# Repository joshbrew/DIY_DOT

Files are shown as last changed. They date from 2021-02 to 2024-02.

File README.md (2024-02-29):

# DIY Diffuse Optical Tomography (DOT) PCB plans

Testing low cost 28 sensor DOT. This repo will be getting updated as I get results and some working code to share. I will share how to drive the LEDs and how I get simultaneous sensor output as I get things demonstrable.

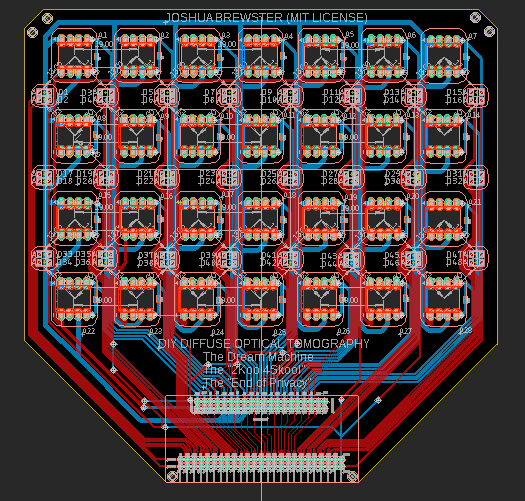
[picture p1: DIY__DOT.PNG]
DIYDOT


DIY DOT flexible sensor design based on [this 2007 Retinotopic mapping paper](https://www.pnas.org/content/104/29/12169) for a simple and modular 28 channel high-density optical tomography headset. The question I want to answer: can I get [deep image reconstruction](https://journals.plos.org/ploscompbiol/article?id=10.1371/journal.pcbi.1006633)?

This design uses 28 OPT101s and 24 pairs (48 total) 1206 sized generic LED pairs of whatever wavelength you want. The OPT101s can have the gain turned up by adding a cap and resistor between the right pins [see datasheet](https://www.ti.com/lit/ds/symlink/opt101.pdf?HQS=TI-null-null-alldatasheets-df-pf-SEP-wwe). You can get really cheap ones on Aliexpress that work consistently.

Use a site like PCBway for cheap flex PCBs. There is FR4 stiffener on both sides. This is meant to be hand-assembled, careful not to burn the pads or sensitive OPT101 pins (i.e. use low temperature solder for testing). Pop the OPT101s (notch facing left from the front) in through the back to make them flush with the stiffener and solder from back.  

# 16 channel (forehead-friendly)

New (cheapo version):
Capture1

New (includes transimpedance amps):
Capture2

Old:
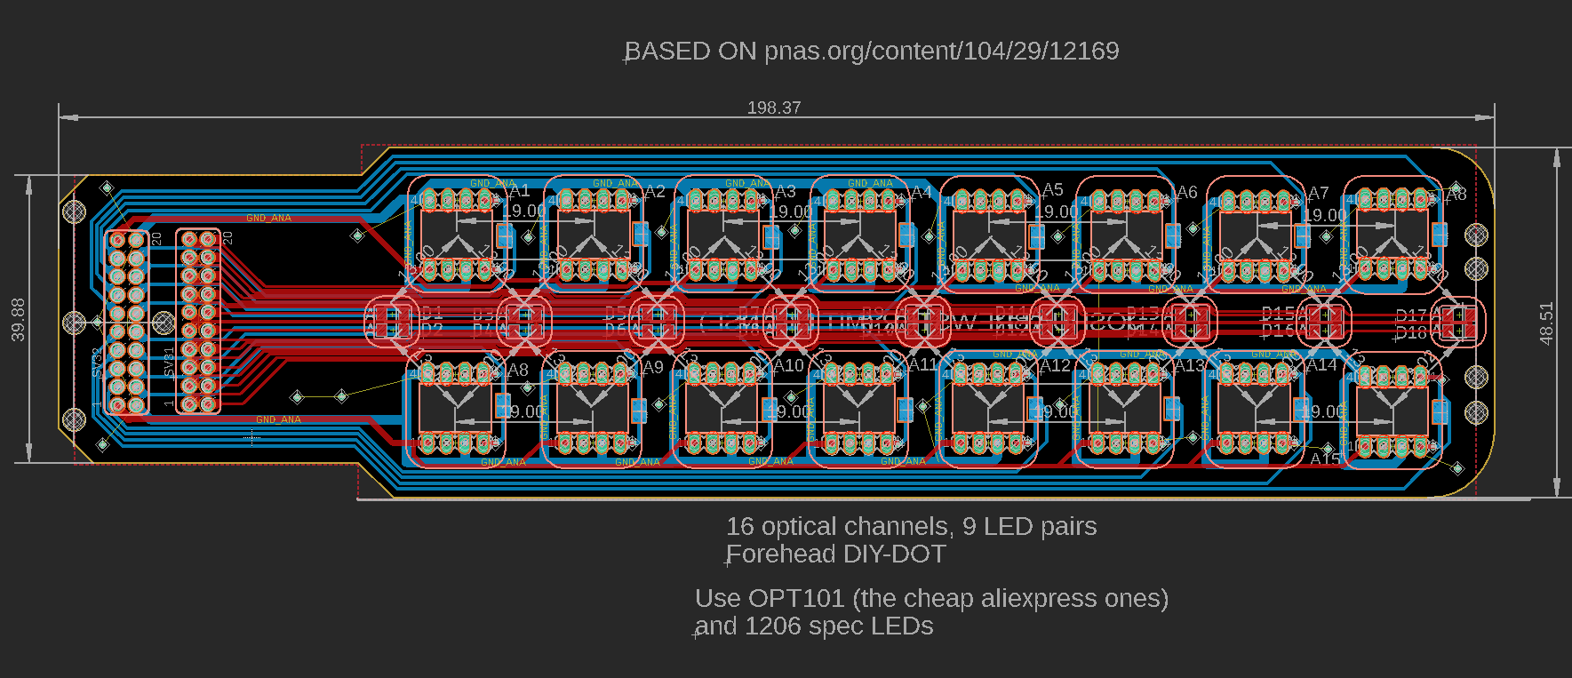
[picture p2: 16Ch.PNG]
DIY16DOT


# For LED Driver we're using the $4 RP2040 mini, drivers WIP and docs etc.

# WIP Software for capture and simulation:

3D simulation with BabylonJS:
- https://github.com/joshbrew/DIY_DOT/tree/main/js/bananas
Recording test for our nRF5x boards (WIP connector/carrier board incoming after we test it):
- https://github.com/joshbrew/DIY_DOT/tree/main/js/record_nirs

The simulation math needs help but we'll figure it out eventually.

### What you need to make it work:
* LED driver microcontroller with PWM driver, we've got a WIP firmware for the RP2040 
* 48 GPIO or some kind of relay to drive the LEDs which need to be flashed independently. Can be done by stringing multiple cheap boards together via RX/TX pins (will publish examples eventually). 
* We recommend narrow-coned LEDs to minimize scalp interference for short separation channels.
* Add light pipes over PD and LED areas to get better contact.
* [Use >1000nm IR LEDs for best penetration. (no idea if they exist at this size)](https://www.spiedigitallibrary.org/journals/journal-of-biomedical-optics/volume-25/issue-09/097003/Diffuse-correlation-spectroscopy-measurements-of-blood-flow-using-1064nm-light/10.1117/1.JBO.25.9.097003.full?fbclid=IwAR02-l_q-xCykuuqUjc_RWJfQE7ESOEIRK0G9mqZSWaGiFhfwu1QNV42vjQ&SSO=1) The other LED can be red, green, or another IR wavelength (e.g. 850nm).

## What can I do with this?

Read about fMRI, then assume this is an fMRI but it's dirt cheap in comparison. However, it only gets you the few outer centimeters of depth resolution, which can be enhanced with higher power lighting, guassian windows, interferometry (the most interesting next logical step for this ala OCT), and some other classic filtering tricks from RF and astronomy. So we can do legit mind reading, source localization for EEG, brain topology studies, and potentially real time monitoring of problems like subdural hematoma or possible metabolic issues in the high energy-demanding neocortex. Multimodal imaging promises to solve a lot of modeling problems with this technology, and there's probably a lot more to learn just in terms of how different physiology contains relevant computational information and what the interplay is. That's my very unqualified 2 cents :P

## License 
MIT License: Do whatever you want with it, I'm gonna do what I want with it too. And cite this repo if you make it useful! 
Get in touch @ brewster.joshua1@gmail.com, I'm working on a scalable version of this stuff but it just takes forever between factory times and me not knowing what the hell I'm doing.

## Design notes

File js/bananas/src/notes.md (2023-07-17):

## Sample rates
1000/250sps = 4ms per sample.
500sps = 2ms per sample
1000sps = 1ms per sample
2000sps = .5ms per sample 

Max is 32000 but that's really high for normal laptops/phones without SAI.

e.g 9 samples (1 ble packet) = 4ms*9 = 36ms

## Bitrates
Max BLE5 is 2Mbits ideal (but probably not that high in practice)

250 * 16 * 3 * 24 = 288,000bits (288kbits/s) which is good
500sps = 576,000bits (576kbits/s) still good
1000sps = 1,152,000bits (576kbits/s) still good
2000 * 16 * 3 * 24 = 2,304,000bits (2.304mbits/s). too high

## Effective sampling rate for a set of 18 LEDs + 1 ambient reading
1000ms / (18 leds + 1 amb) = 
52.63ms for  1sps effective sampling by amount of time each LED is illuminated / ambient is read
26.16ms for  2sps
13.16ms for  4sps
6.58ms for   8sps

60fps would be 
0.88ms for (18 leds + 1 amb)
1.85ms for (9  leds + 1 amb)

30fps would be
1.85ms for (18 leds + 1 amb)
3.70ms for (9  leds + 1 amb)

20fps would be 
2.63ms for (18 leds + 1 amb)
5.26ms for (9  leds + 1 amb)

## Todos

- Need to implement Modified Beer Lambert's Law
- Need to implement sphere model
- Get Rayleigh scattering model working
- swizzle with real data

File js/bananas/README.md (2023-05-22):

## Diffuse Optical Tomography sim

Simulating paths and overlaps for LED and photodiode arrays, and simulating volumetric data. WIP web driver project for the 16 channel headset.

Capture

NodeJS web app.

`npm i -g tinybuild` or `npm i tinybuild`

then 

`npm start` or `tinybuild`

Then find the local server link in the terminal.

## TODO

- Add a head and brain model for zest
- Connect live data and calibrate the visual further.
- Make the light paths more accurate and diffuse to cover wider volumes. Amplify the representation of fainter readings deeper in for a better image.
- Only require voxel generation the first time with a loading indicator, then save all of the generated indices in IndexedDB so we don't need to iterate the entire sphere with box meshes again. Include something pregenerated as an asset and just check if your parameters match up to decide if to regenerate the model.
- Also do 2D representation

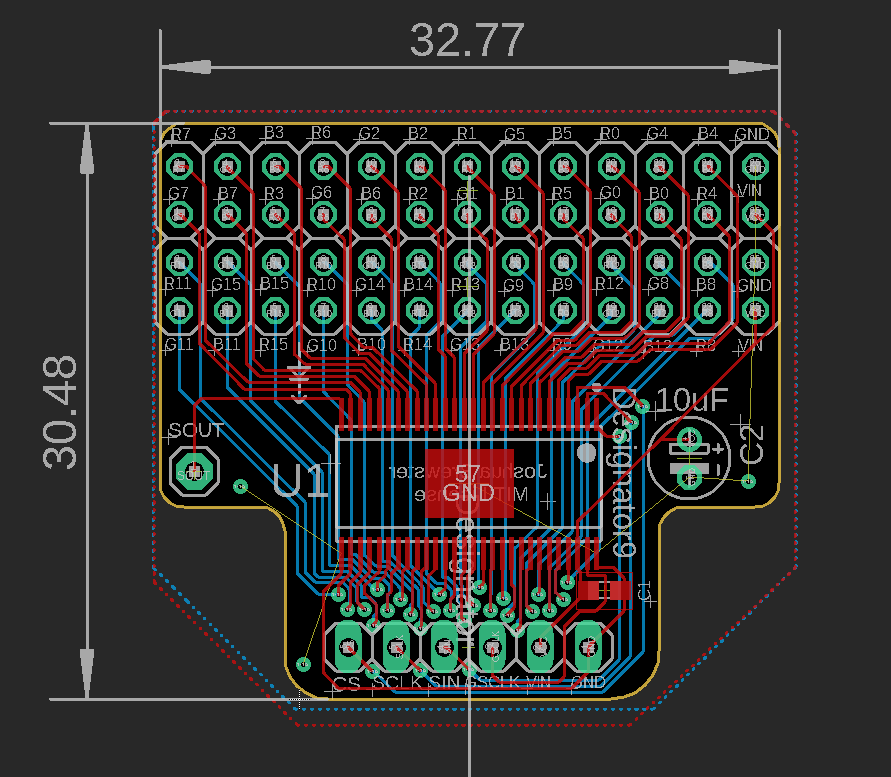
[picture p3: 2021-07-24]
LEDdriver.PNG

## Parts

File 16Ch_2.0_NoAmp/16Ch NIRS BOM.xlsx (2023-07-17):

Designation | Part # | Alt | Description | Mouser/Digikey Link |  | Notes
D19-D34 | BPW 34 or BPW 34S |  | Photodiode, High sensitivity | https://www.mouser.com/c/?q=bpw34 | https://www.mouser.com/ProductDetail/ams-OSRAM/BPW-34-S?qs=vLWxofP3U2zVT0CDmWwS1A%3D%3D
D1-D17 (odd) | MP-2835-1100-FR (far red) | XZM2CRK55W-3 (red) | Far Red 740nm or Red 660nm LED | https://www.digikey.com/en/products/detail/sunled/XZM2CRK55W-3/4901982 | https://www.mouser.com/ProductDetail/Luminus-Devices/MP-2835-1100-FR?qs=DRkmTr78QARZP5ubuC89%252BA%3D%3D | Domed LEDs are better as they focus the light forward, halfway to a laser beam
D2-D18 (even) | XZTHI55W-3 (880nm) | XZTNI55W-3 (940nm) | Infrared 880nm or 940nm LED | https://www.digikey.com/en/products/detail/sunled/XZTHI55W-3/4902102 | https://www.digikey.com/en/products/detail/sunled/XZTNI55W-3/4902105?s=N4IgTCBcDaIBoC0AqA5AkgVgwdQLQGYQBdAXyA
Resistors | RNMF14FTC1M00 (https://www.mouser.com/ProductDetail/SEI-Stackpole/RNMF14FTC1M00?qs=FESYatJ8odK2Y1zZ%2FXv5kg%3D%3D) |  | 1MOhm metal film resistor | RNMF14FTC1M00 (https://www.mouser.com/ProductDetail/SEI-Stackpole/RNMF14FTC1M00?qs=FESYatJ8odK2Y1zZ%2FXv5kg%3D%3D) |  | or whatever
Capacitors | C410C201JAG5TA (https://www.mouser.com/ProductDetail/KEMET/C410C201JAG5TA?qs=QTajy0ParP6iJ%2Fv5ZG4J%252Bw%3D%3D) |  | 200pF capacitor | C410C201JAG5TA (https://www.mouser.com/ProductDetail/KEMET/C410C201JAG5TA?qs=QTajy0ParP6iJ%2Fv5ZG4J%252Bw%3D%3D) |  | or whatever, just needs to be small
SV31, SV32 | M20-7831046 (https://www.mouser.com/ProductDetail/Harwin/M20-7831046?qs=vF78I%252BjhbY%252BXDATeu1%252BhjQ%3D%3D) |  | 10+10 female header |  |  | Mount backside so socket sits on the stiffener and is soldered on exposed front pads

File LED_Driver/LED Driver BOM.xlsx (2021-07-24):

Designation | Part | Qty | Part #
U1 | 48Ch LED Driver | 1 | TLC5955DCAR
C1 | 0602 Cap | 1 | LMK107BBJ106KALT
C2 | 4mm Electrolytic | 1 | USW1C100MDD1TP
 | Total Ct: | 3

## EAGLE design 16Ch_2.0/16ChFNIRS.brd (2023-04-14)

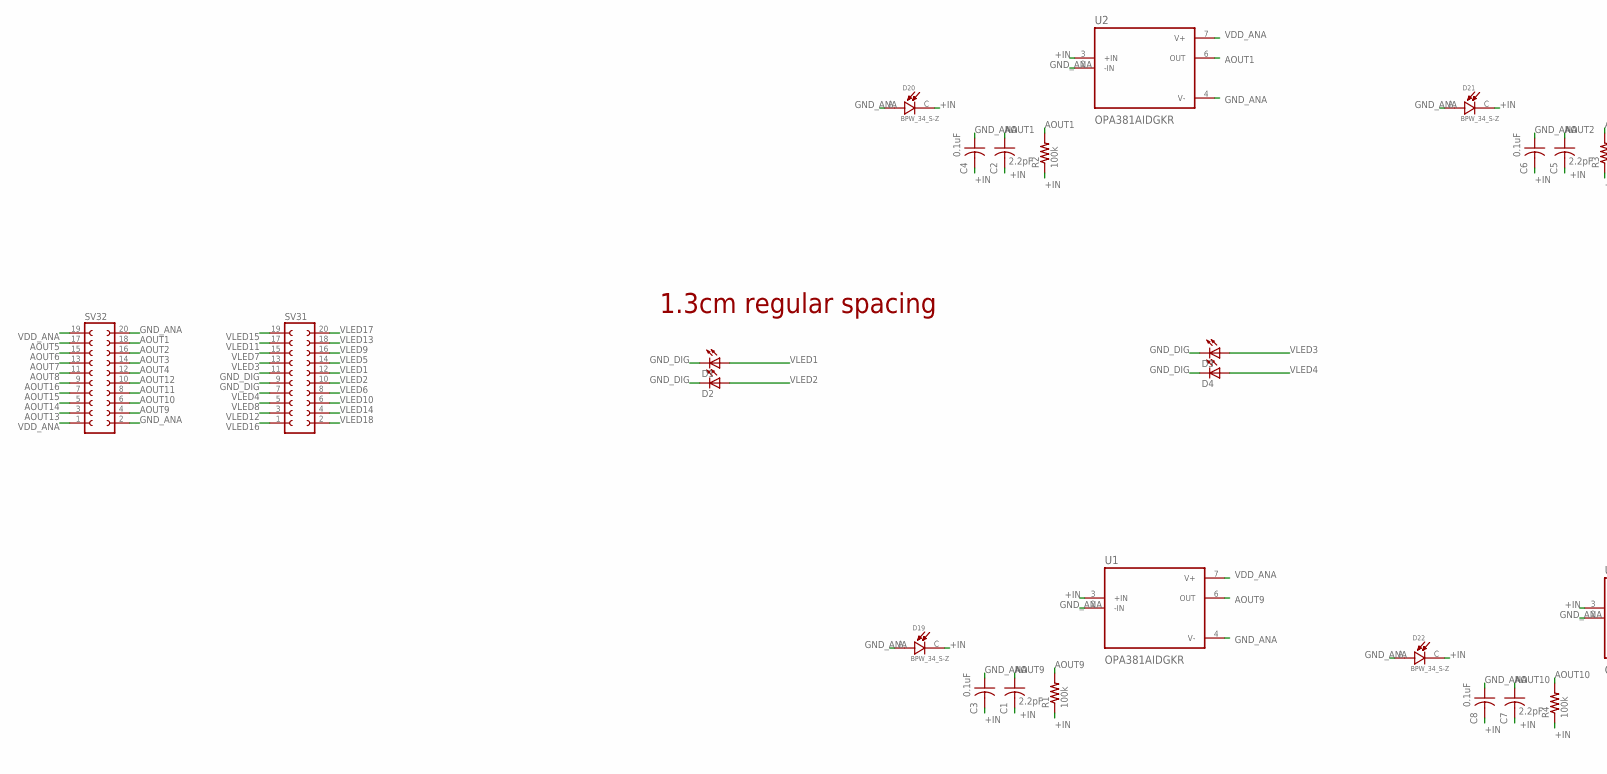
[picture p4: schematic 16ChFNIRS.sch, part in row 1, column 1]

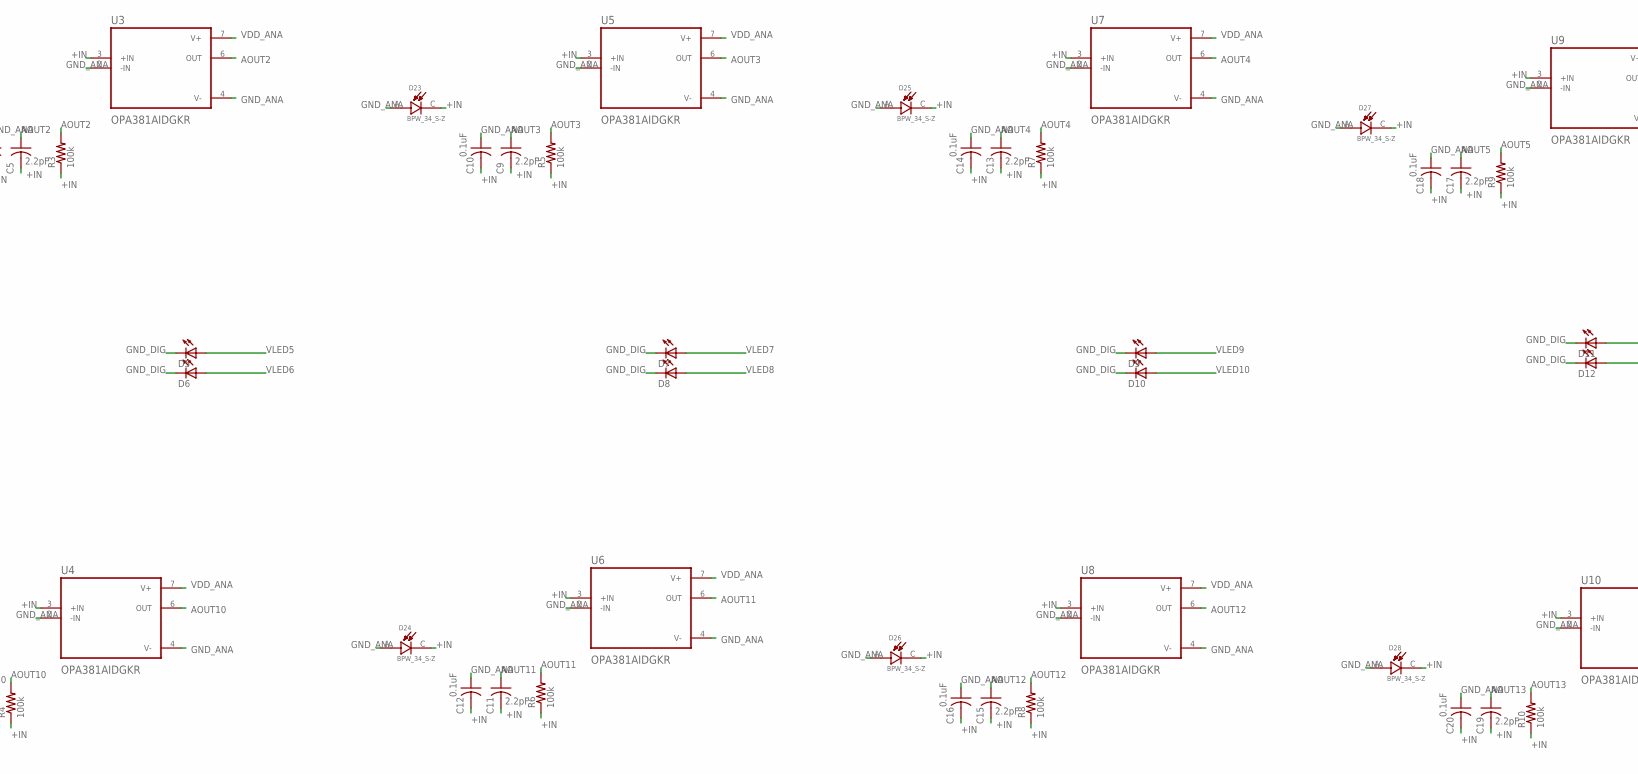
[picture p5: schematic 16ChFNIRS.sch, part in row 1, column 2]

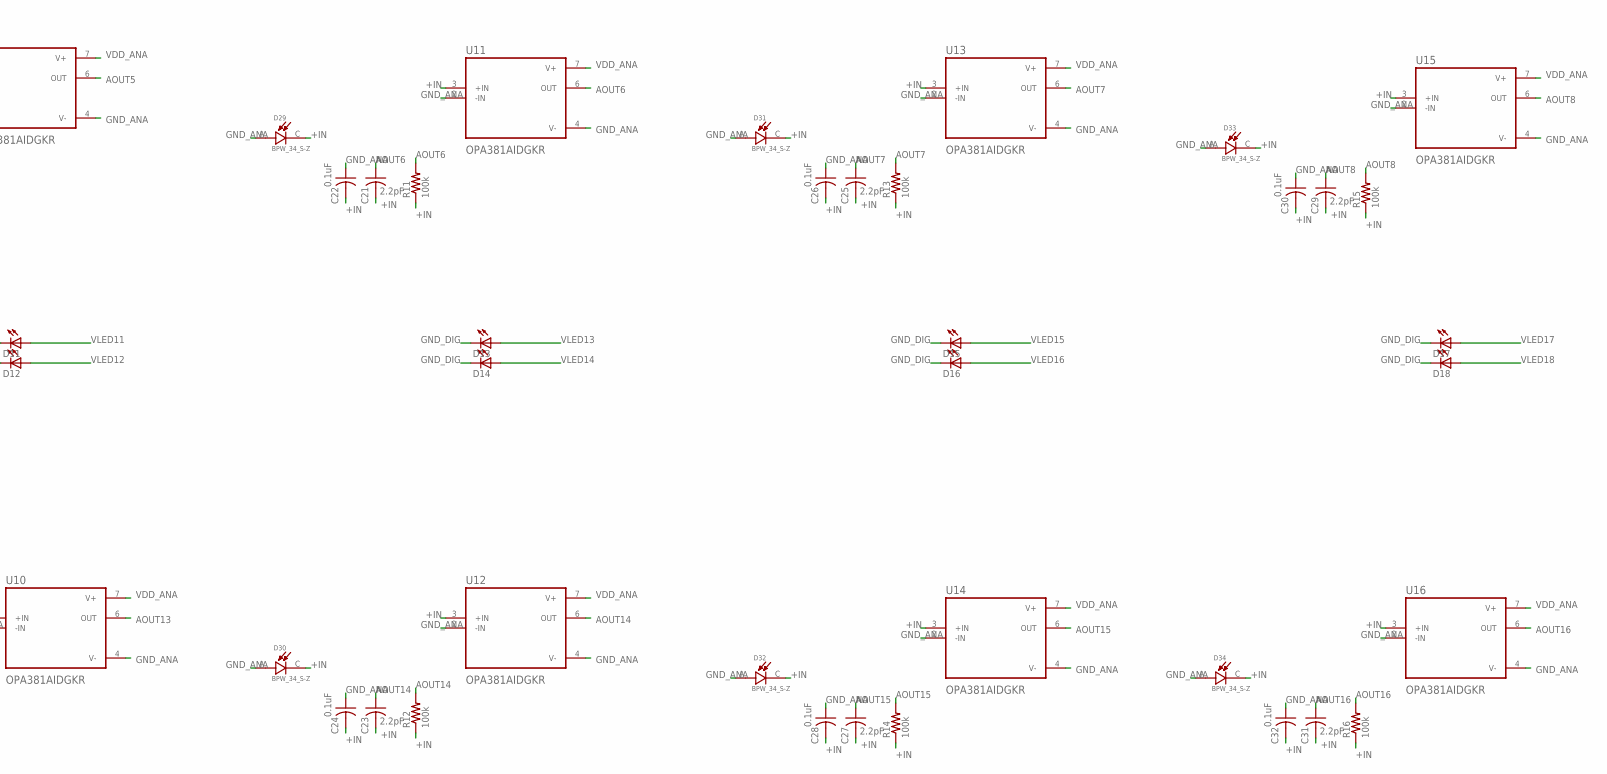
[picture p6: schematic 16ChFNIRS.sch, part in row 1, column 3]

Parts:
C1, C2, C5, C7, C9, C11, C13, C15, C17, C19, C21, C23, C25, C27, C29, C31: 2.2pF; C0603K
C3, C4, C6, C8, C10, C12, C14, C16, C18, C20, C22, C24, C26, C28, C30, C32: 0.1uF; C0603K
D1, D2, D3, D4, D5, D6, D7, D8, D9, D10, D11, D12, D13, D14, D15, D16, D17, D18: LED1206; LED-1206
D19, D20, D21, D22, D23, D24, D25, D26, D27, D28, D29, D30, D31, D32, D33, D34: BPW_34_S-Z; DIO_BPW_34_S-Z
R1, R2, R3, R4, R5, R6, R7, R8, R9, R10, R11, R12, R13, R14, R15, R16: 100k; R0603
SV31, SV32: FE10-2
U1, U2, U3, U4, U5, U6, U7, U8, U9, U10, U11, U12, U13, U14, U15, U16: OPA381AIDGKR; SOP65P490X110-8N

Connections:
+IN: C1.2, C2.2, C3.2, C4.2, C5.2, C6.2, C7.2, C8.2, C9.2, C10.2, C11.2, C12.2, C13.2, C14.2, C15.2, C16.2, C17.2, C18.2, C19.2, C20.2, C21.2, C22.2, C23.2, C24.2, C25.2, C26.2, C27.2, C28.2, C29.2, C30.2, C31.2, C32.2, D19.C, D20.C, D21.C, D22.C, D23.C, D24.C, D25.C, D26.C, D27.C, D28.C, D29.C, D30.C, D31.C, D32.C, D33.C, D34.C, R1.1, R2.1, R3.1, R4.1, R5.1, R6.1, R7.1, R8.1, R9.1, R10.1, R11.1, R12.1, R13.1, R14.1, R15.1, R16.1, U1.3 (+IN), U2.3 (+IN), U3.3 (+IN), U4.3 (+IN), U5.3 (+IN), U6.3 (+IN), U7.3 (+IN), U8.3 (+IN), U9.3 (+IN), U10.3 (+IN), U11.3 (+IN), U12.3 (+IN), U13.3 (+IN), U14.3 (+IN), U15.3 (+IN), U16.3 (+IN)
AOUT1: C2.1, R2.2, SV32.18, U2.6 (OUT)
AOUT2: C5.1, R3.2, SV32.16, U3.6 (OUT)
AOUT3: C9.1, R5.2, SV32.14, U5.6 (OUT)
AOUT4: C13.1, R7.2, SV32.12, U7.6 (OUT)
AOUT5: C17.1, R9.2, SV32.17, U9.6 (OUT)
AOUT6: C21.1, R11.2, SV32.15, U11.6 (OUT)
AOUT7: C25.1, R13.2, SV32.13, U13.6 (OUT)
AOUT8: C29.1, R15.2, SV32.11, U15.6 (OUT)
AOUT9: C1.1, R1.2, SV32.4, U1.6 (OUT)
AOUT10: C7.1, R4.2, SV32.6, U4.6 (OUT)
AOUT11: C11.1, R6.2, SV32.8, U6.6 (OUT)
AOUT12: C15.1, R8.2, SV32.10, U8.6 (OUT)
AOUT13: C19.1, R10.2, SV32.3, U10.6 (OUT)
AOUT14: C23.1, R12.2, SV32.5, U12.6 (OUT)
AOUT15: C27.1, R14.2, SV32.7, U14.6 (OUT)
AOUT16: C31.1, R16.2, SV32.9, U16.6 (OUT)
GND_ANA: C3.1, C4.1, C6.1, C8.1, C10.1, C12.1, C14.1, C16.1, C18.1, C20.1, C22.1, C24.1, C26.1, C28.1, C30.1, C32.1, D19.A, D20.A, D21.A, D22.A, D23.A, D24.A, D25.A, D26.A, D27.A, D28.A, D29.A, D30.A, D31.A, D32.A, D33.A, D34.A, SV32.2, SV32.20, U1.2 (-IN), U1.4 (V-), U2.2 (-IN), U2.4 (V-), U3.2 (-IN), U3.4 (V-), U4.2 (-IN), U4.4 (V-), U5.2 (-IN), U5.4 (V-), U6.2 (-IN), U6.4 (V-), U7.2 (-IN), U7.4 (V-), U8.2 (-IN), U8.4 (V-), U9.2 (-IN), U9.4 (V-), U10.2 (-IN), U10.4 (V-), U11.2 (-IN), U11.4 (V-), U12.2 (-IN), U12.4 (V-), U13.2 (-IN), U13.4 (V-), U14.2 (-IN), U14.4 (V-), U15.2 (-IN), U15.4 (V-), U16.2 (-IN), U16.4 (V-)
GND_DIG: D1.C, D2.C, D3.C, D4.C, D5.C, D6.C, D7.C, D8.C, D9.C, D10.C, D11.C, D12.C, D13.C, D14.C, D15.C, D16.C, D17.C, D18.C, SV31.9, SV31.11
VDD_ANA: SV32.1, SV32.19, U1.7 (V+), U2.7 (V+), U3.7 (V+), U4.7 (V+), U5.7 (V+), U6.7 (V+), U7.7 (V+), U8.7 (V+), U9.7 (V+), U10.7 (V+), U11.7 (V+), U12.7 (V+), U13.7 (V+), U14.7 (V+), U15.7 (V+), U16.7 (V+)
VLED1: D1.A, SV31.12
VLED2: D2.A, SV31.10
VLED3: D3.A, SV31.13
VLED4: D4.A, SV31.7
VLED5: D5.A, SV31.14
VLED6: D6.A, SV31.8
VLED7: D7.A, SV31.15
VLED8: D8.A, SV31.5
VLED9: D9.A, SV31.16
VLED10: D10.A, SV31.6
VLED11: D11.A, SV31.17
VLED12: D12.A, SV31.3
VLED13: D13.A, SV31.18
VLED14: D14.A, SV31.4
VLED15: D15.A, SV31.19
VLED16: D16.A, SV31.1
VLED17: D17.A, SV31.20
VLED18: D18.A, SV31.2

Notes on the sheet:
1.3cm regular spacing

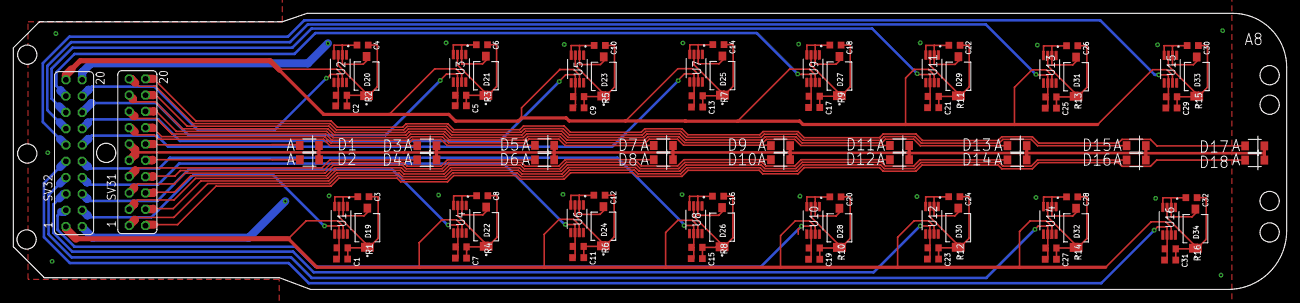
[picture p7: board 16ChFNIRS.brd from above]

Board: 2 copper layers, 198.4 x 43.0 mm, 100 parts (0 on the bottom side), 38 nets.

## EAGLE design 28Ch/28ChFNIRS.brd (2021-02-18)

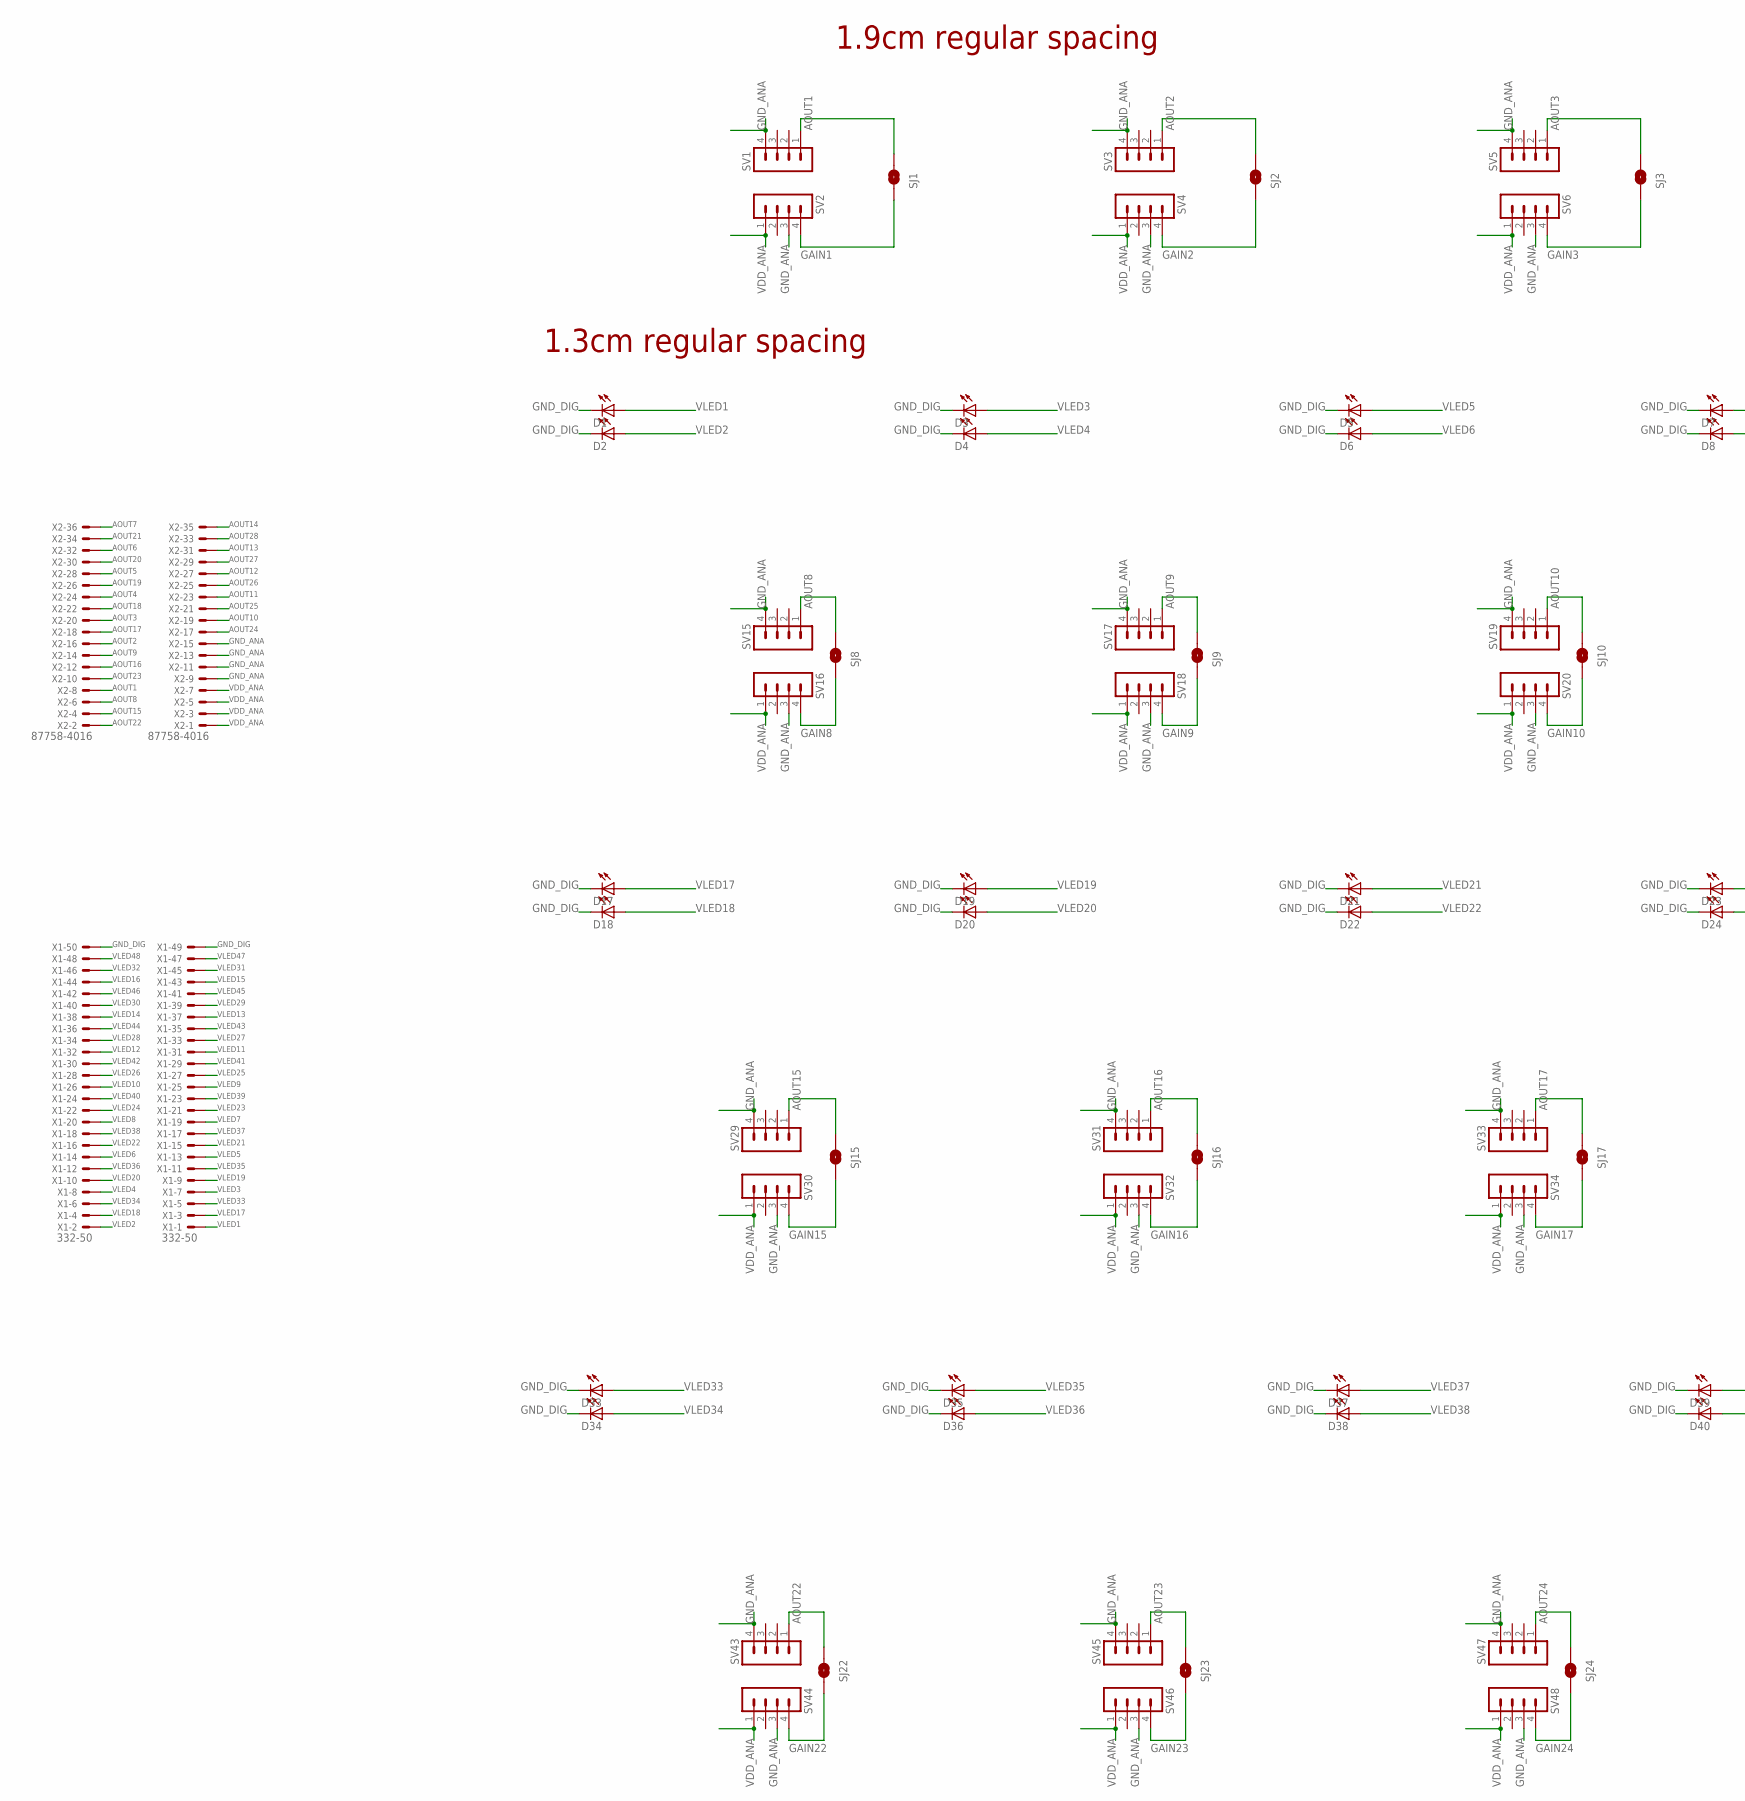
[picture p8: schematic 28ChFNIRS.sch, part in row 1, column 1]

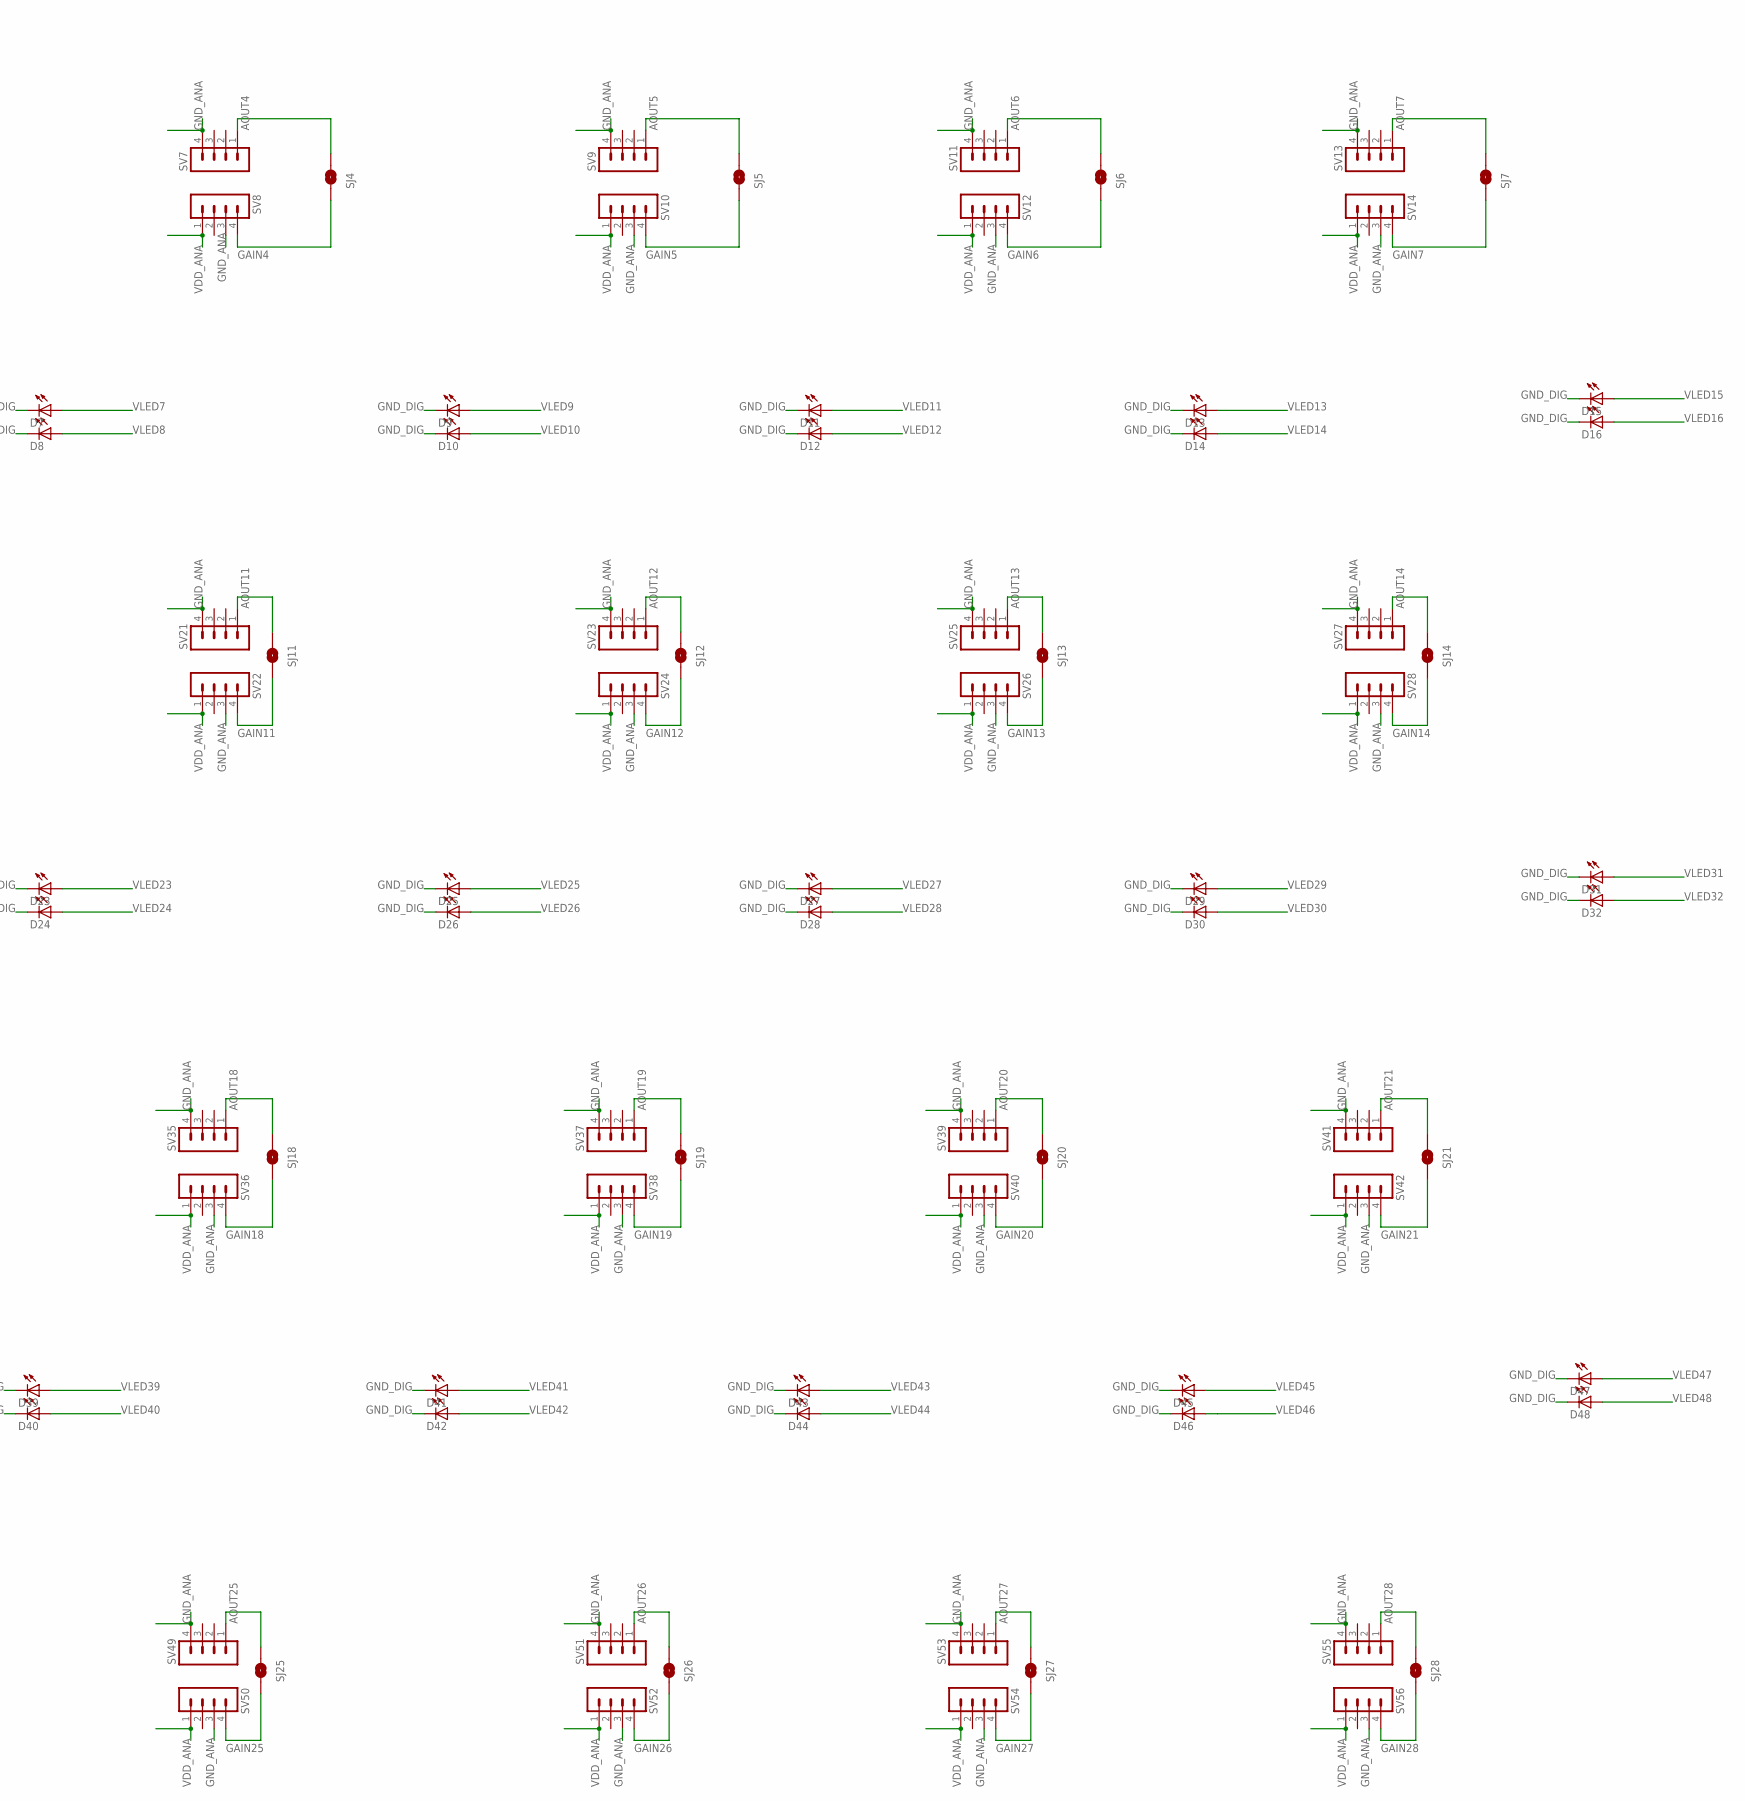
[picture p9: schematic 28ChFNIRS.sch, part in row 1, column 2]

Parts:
D1, D2, D3, D4, D5, D6, D7, D8, D9, D10, D11, D12, D13, D14, D15, D16, D17, D18, D19, D20, D21, D22, D23, D24, D25, D26, D27, D28, D29, D30, D31, D32, D33, D34, D35, D36, D37, D38, D39, D40, D41, D42, D43, D44, D45, D46, D47, D48: LED1206; LED-1206
SJ1, SJ2, SJ3, SJ4, SJ5, SJ6, SJ7, SJ8, SJ9, SJ10, SJ11, SJ12, SJ13, SJ14, SJ15, SJ16, SJ17, SJ18, SJ19, SJ20, SJ21, SJ22, SJ23, SJ24, SJ25, SJ26, SJ27, SJ28: SOLDERJUMPERNC; SJ_2S_SMALL
SV1, SV2, SV3, SV4, SV5, SV6, SV7, SV8, SV9, SV10, SV11, SV12, SV13, SV14, SV15, SV16, SV17, SV18, SV19, SV20, SV21, SV22, SV23, SV24, SV25, SV26, SV27, SV28, SV29, SV30, SV31, SV32, SV33, SV34, SV35, SV36, SV37, SV38, SV39, SV40, SV41, SV42, SV43, SV44, SV45, SV46, SV47, SV48, SV49, SV50, SV51, SV52, SV53, SV54, SV55, SV56: MA04-1
X1: 332-50
X2: 87758-4016

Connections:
AOUT1: SJ1.2, SV1.1, X2.8
AOUT2: SJ2.2, SV3.1, X2.16
AOUT3: SJ3.2, SV5.1, X2.20
AOUT4: SJ4.2, SV7.1, X2.24
AOUT5: SJ5.2, SV9.1, X2.28
AOUT6: SJ6.2, SV11.1, X2.32
AOUT7: SJ7.2, SV13.1, X2.36
AOUT8: SJ8.2, SV15.1, X2.6
AOUT9: SJ9.2, SV17.1, X2.14
AOUT10: SJ10.2, SV19.1, X2.19
AOUT11: SJ11.2, SV21.1, X2.23
AOUT12: SJ12.2, SV23.1, X2.27
AOUT13: SJ13.2, SV25.1, X2.31
AOUT14: SJ14.2, SV27.1, X2.35
AOUT15: SJ15.2, SV29.1, X2.4
AOUT16: SJ16.2, SV31.1, X2.12
AOUT17: SJ17.2, SV33.1, X2.18
AOUT18: SJ18.2, SV35.1, X2.22
AOUT19: SJ19.2, SV37.1, X2.26
AOUT20: SJ20.2, SV39.1, X2.30
AOUT21: SJ21.2, SV41.1, X2.34
AOUT22: SJ22.2, SV43.1, X2.2
AOUT23: SJ23.2, SV45.1, X2.10
AOUT24: SJ24.2, SV47.1, X2.17
AOUT25: SJ25.2, SV49.1, X2.21
AOUT26: SJ26.2, SV51.1, X2.25
AOUT27: SJ27.2, SV53.1, X2.29
AOUT28: SJ28.2, SV55.1, X2.33
GAIN1: SJ1.1, SV2.4
GAIN2: SJ2.1, SV4.4
GAIN3: SJ3.1, SV6.4
GAIN4: SJ4.1, SV8.4
GAIN5: SJ5.1, SV10.4
GAIN6: SJ6.1, SV12.4
GAIN7: SJ7.1, SV14.4
GAIN8: SJ8.1, SV16.4
GAIN9: SJ9.1, SV18.4
GAIN10: SJ10.1, SV20.4
GAIN11: SJ11.1, SV22.4
GAIN12: SJ12.1, SV24.4
GAIN13: SJ13.1, SV26.4
GAIN14: SJ14.1, SV28.4
GAIN15: SJ15.1, SV30.4
GAIN16: SJ16.1, SV32.4
GAIN17: SJ17.1, SV34.4
GAIN18: SJ18.1, SV36.4
GAIN19: SJ19.1, SV38.4
GAIN20: SJ20.1, SV40.4
GAIN21: SJ21.1, SV42.4
GAIN22: SJ22.1, SV44.4
GAIN23: SJ23.1, SV46.4
GAIN24: SJ24.1, SV48.4
GAIN25: SJ25.1, SV50.4
GAIN26: SJ26.1, SV52.4
GAIN27: SJ27.1, SV54.4
GAIN28: SJ28.1, SV56.4
GND_ANA: SV1.4, SV2.3, SV3.4, SV4.3, SV5.4, SV6.3, SV7.4, SV8.3, SV9.4, SV10.3, SV11.4, SV12.3, SV13.4, SV14.3, SV15.4, SV16.3, SV17.4, SV18.3, SV19.4, SV20.3, SV21.4, SV22.3, SV23.4, SV24.3, SV25.4, SV26.3, SV27.4, SV28.3, SV29.4, SV30.3, SV31.4, SV32.3, SV33.4, SV34.3, SV35.4, SV36.3, SV37.4, SV38.3, SV39.4, SV40.3, SV41.4, SV42.3, SV43.4, SV44.3, SV45.4, SV46.3, SV47.4, SV48.3, SV49.4, SV50.3, SV51.4, SV52.3, SV53.4, SV54.3, SV55.4, SV56.3, X2.9, X2.11, X2.13, X2.15
GND_DIG: D1.C, D2.C, D3.C, D4.C, D5.C, D6.C, D7.C, D8.C, D9.C, D10.C, D11.C, D12.C, D13.C, D14.C, D15.C, D16.C, D17.C, D18.C, D19.C, D20.C, D21.C, D22.C, D23.C, D24.C, D25.C, D26.C, D27.C, D28.C, D29.C, D30.C, D31.C, D32.C, D33.C, D34.C, D35.C, D36.C, D37.C, D38.C, D39.C, D40.C, D41.C, D42.C, D43.C, D44.C, D45.C, D46.C, D47.C, D48.C, X1.49, X1.50
VDD_ANA: SV2.1, SV4.1, SV6.1, SV8.1, SV10.1, SV12.1, SV14.1, SV16.1, SV18.1, SV20.1, SV22.1, SV24.1, SV26.1, SV28.1, SV30.1, SV32.1, SV34.1, SV36.1, SV38.1, SV40.1, SV42.1, SV44.1, SV46.1, SV48.1, SV50.1, SV52.1, SV54.1, SV56.1, X2.1, X2.3, X2.5, X2.7
VLED1: D1.A, X1.1
VLED2: D2.A, X1.2
VLED3: D3.A, X1.7
VLED4: D4.A, X1.8
VLED5: D5.A, X1.13
VLED6: D6.A, X1.14
VLED7: D7.A, X1.19
VLED8: D8.A, X1.20
VLED9: D9.A, X1.25
VLED10: D10.A, X1.26
VLED11: D11.A, X1.31
VLED12: D12.A, X1.32
VLED13: D13.A, X1.37
VLED14: D14.A, X1.38
VLED15: D15.A, X1.43
VLED16: D16.A, X1.44
VLED17: D17.A, X1.3
VLED18: D18.A, X1.4
VLED19: D19.A, X1.9
VLED20: D20.A, X1.10
VLED21: D21.A, X1.15
VLED22: D22.A, X1.16
VLED23: D23.A, X1.21
VLED24: D24.A, X1.22
VLED25: D25.A, X1.27
VLED26: D26.A, X1.28
VLED27: D27.A, X1.33
VLED28: D28.A, X1.34
VLED29: D29.A, X1.39
VLED30: D30.A, X1.40
VLED31: D31.A, X1.45
VLED32: D32.A, X1.46
VLED33: D33.A, X1.5
VLED34: D34.A, X1.6
VLED35: D35.A, X1.11
VLED36: D36.A, X1.12
VLED37: D37.A, X1.17
VLED38: D38.A, X1.18
VLED39: D39.A, X1.23
VLED40: D40.A, X1.24
VLED41: D41.A, X1.29
VLED42: D42.A, X1.30
VLED43: D43.A, X1.35
VLED44: D44.A, X1.36
VLED45: D45.A, X1.41
VLED46: D46.A, X1.42
VLED47: D47.A, X1.47
VLED48: D48.A, X1.48

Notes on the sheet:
1.3cm regular spacing
1.9cm regular spacing

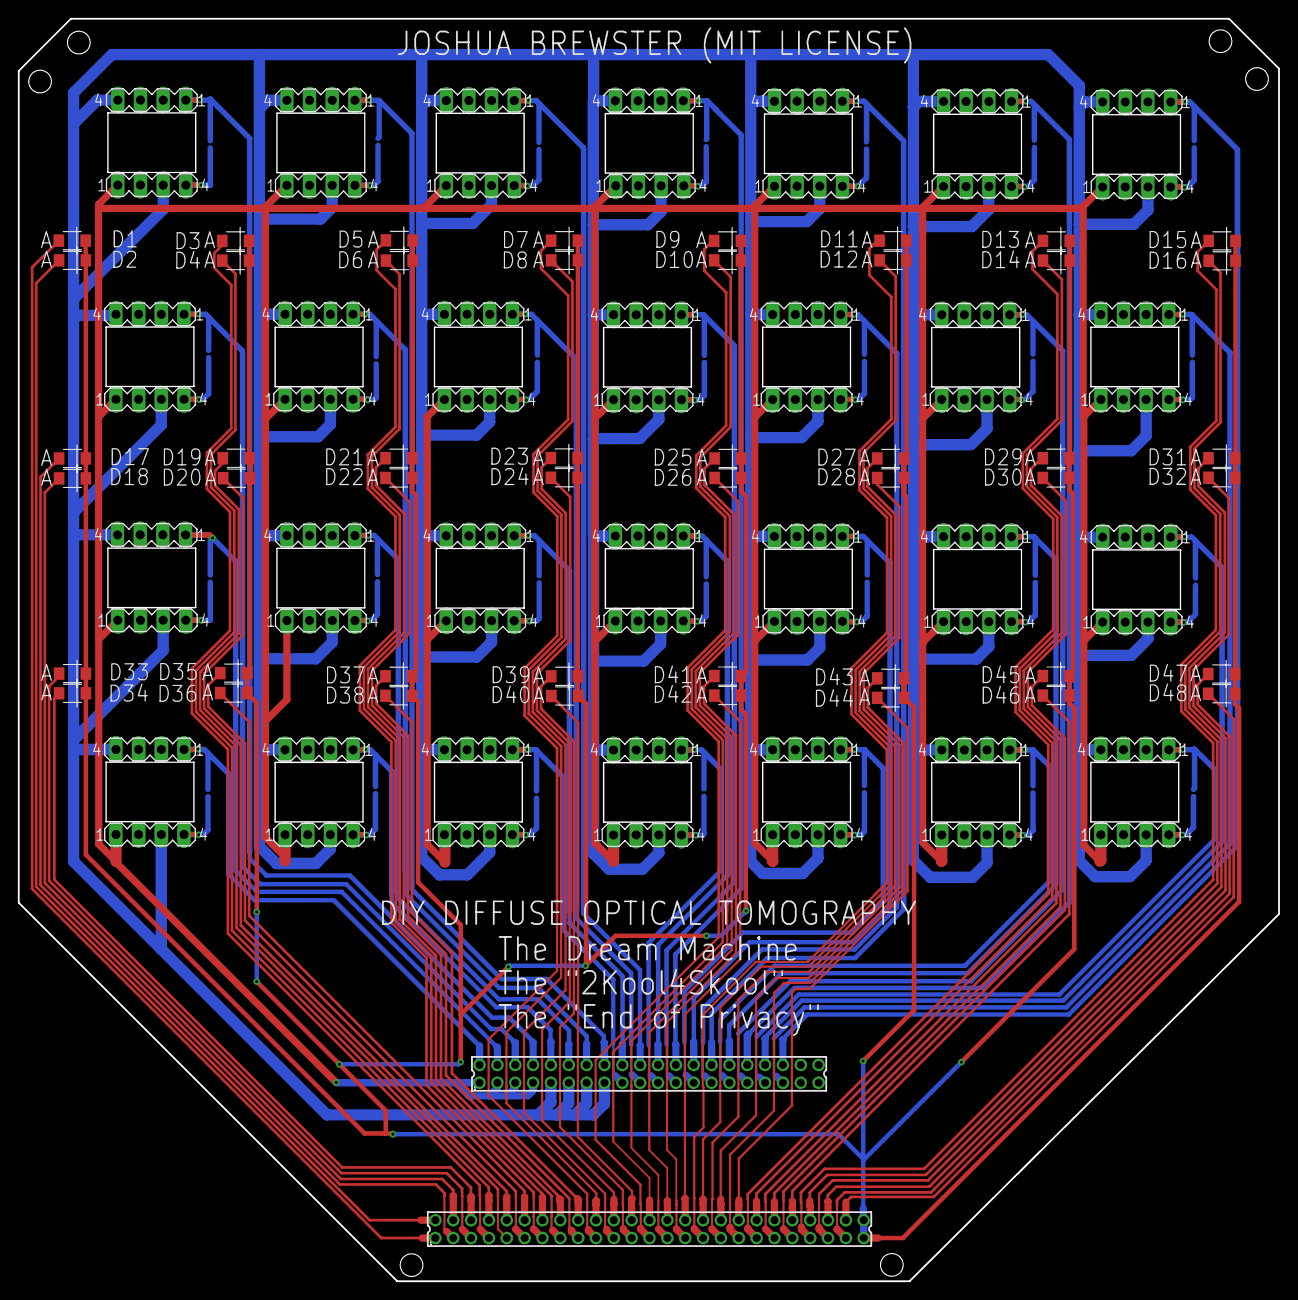
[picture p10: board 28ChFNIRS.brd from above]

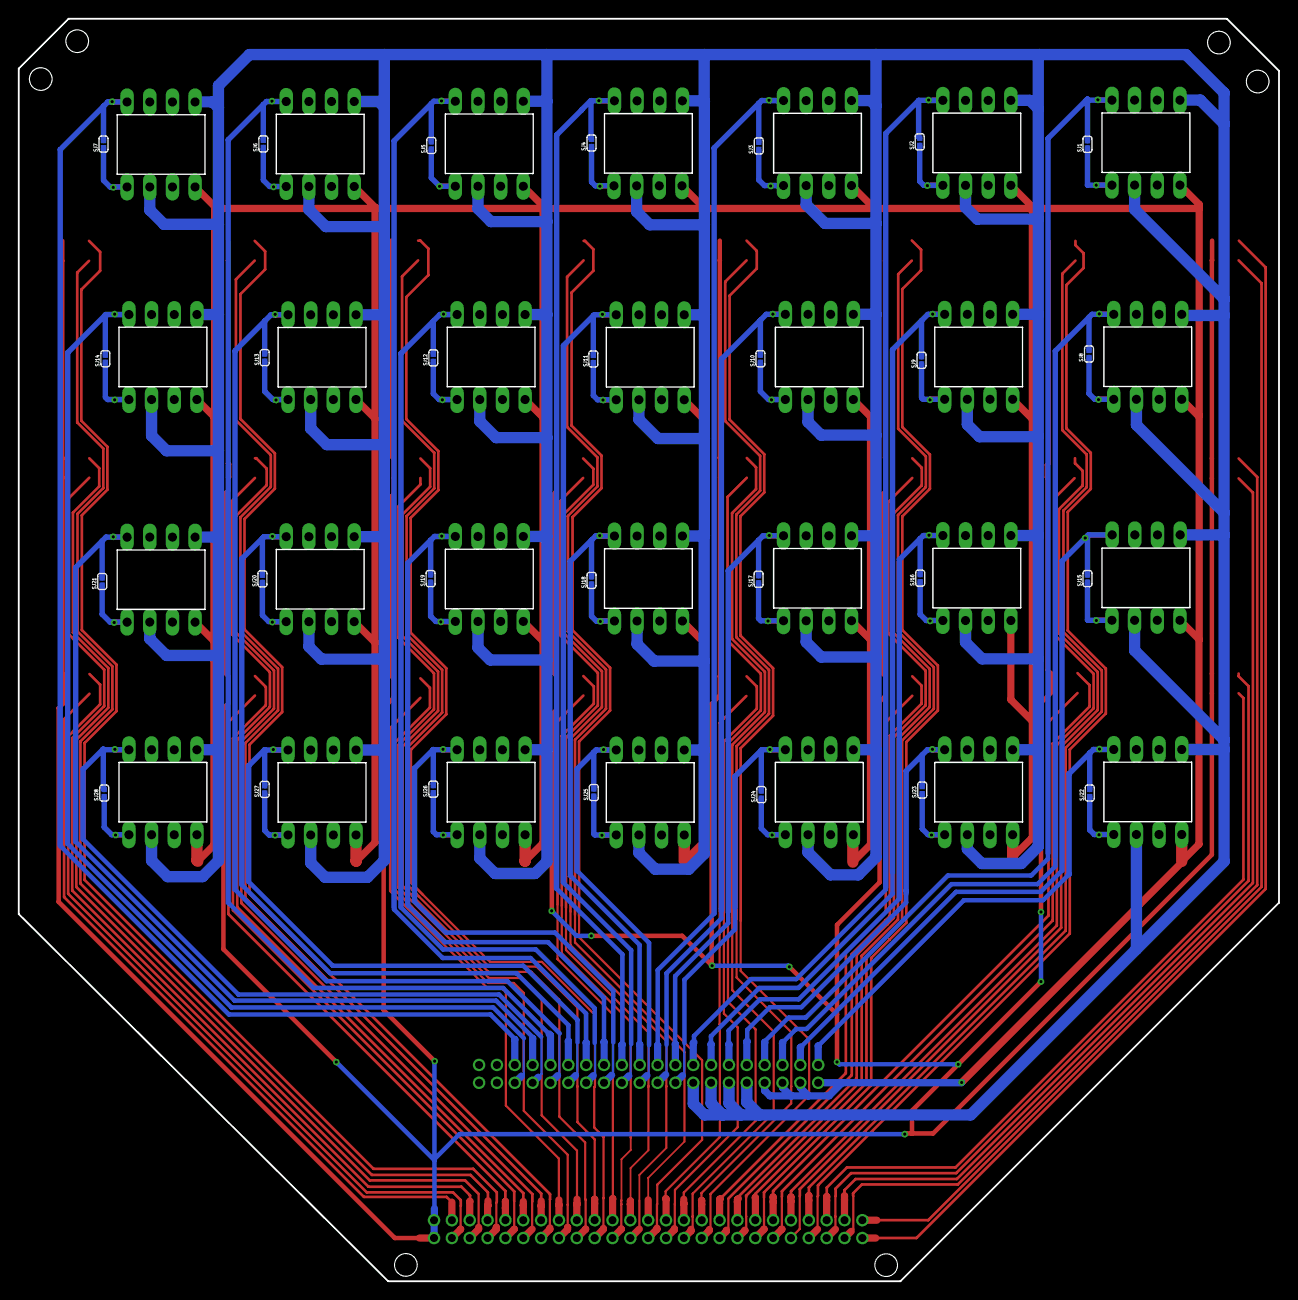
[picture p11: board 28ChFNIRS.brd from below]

Board: 2 copper layers, 141.2 x 141.5 mm, 134 parts (28 on the bottom side), 107 nets.

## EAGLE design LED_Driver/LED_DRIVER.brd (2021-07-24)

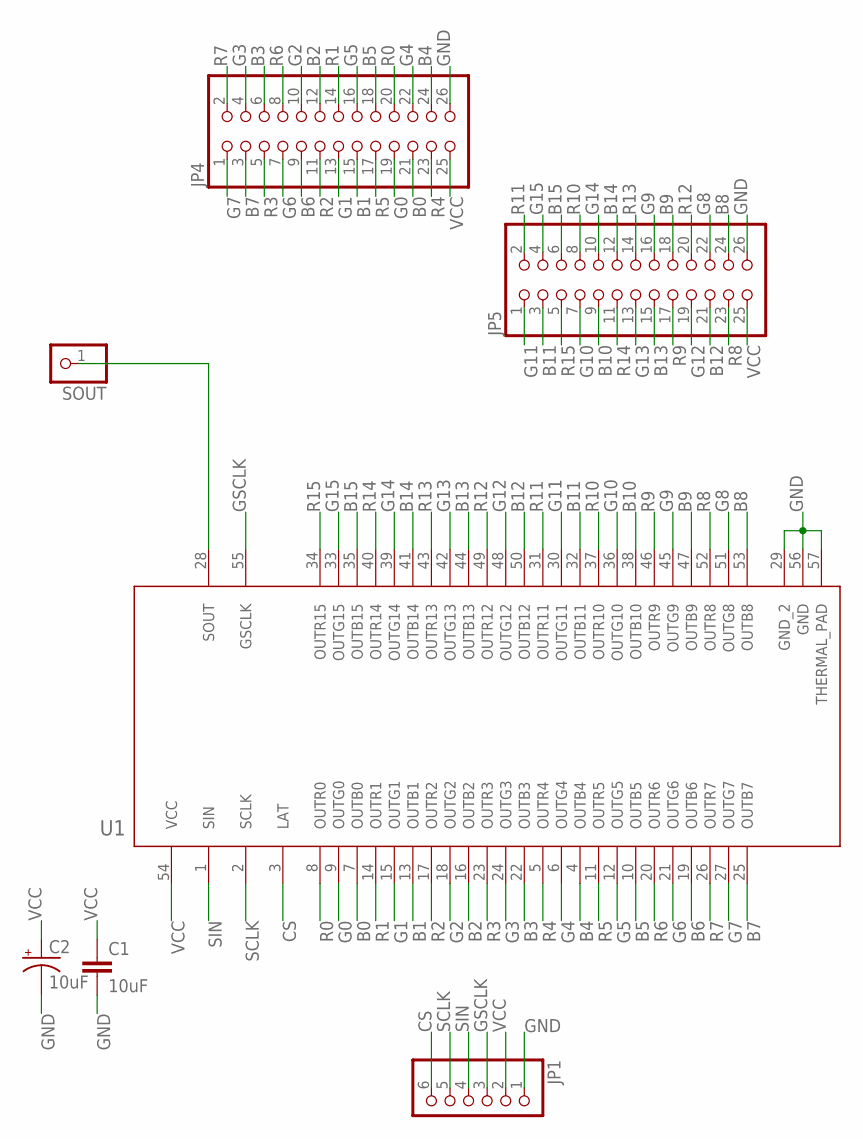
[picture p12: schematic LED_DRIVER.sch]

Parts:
C1: 10uF; C0603
C2: 10uF; E2-4
JP1: PINHD-1X6; 1X06
JP4, JP5: PINHD-2X13; 2X13
SOUT: PINHD-1X1; 1X01
U1: Value; DCA0056F-IPC_B

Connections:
B0: JP4.21, U1.7 (OUTB0)
B1: JP4.15, U1.13 (OUTB1)
B2: JP4.12, U1.16 (OUTB2)
B3: JP4.6, U1.22 (OUTB3)
B4: JP4.24, U1.4 (OUTB4)
B5: JP4.18, U1.10 (OUTB5)
B6: JP4.9, U1.19 (OUTB6)
B7: JP4.3, U1.25 (OUTB7)
B8: JP5.24, U1.53 (OUTB8)
B9: JP5.18, U1.47 (OUTB9)
B10: JP5.9, U1.38 (OUTB10)
B11: JP5.3, U1.32 (OUTB11)
B12: JP5.21, U1.50 (OUTB12)
B13: JP5.15, U1.44 (OUTB13)
B14: JP5.12, U1.41 (OUTB14)
B15: JP5.6, U1.35 (OUTB15)
CS: JP1.6, U1.3 (LAT)
G0: JP4.19, U1.9 (OUTG0)
G1: JP4.13, U1.15 (OUTG1)
G2: JP4.10, U1.18 (OUTG2)
G3: JP4.4, U1.24 (OUTG3)
G4: JP4.22, U1.6 (OUTG4)
G5: JP4.16, U1.12 (OUTG5)
G6: JP4.7, U1.21 (OUTG6)
G7: JP4.1, U1.27 (OUTG7)
G8: JP5.22, U1.51 (OUTG8)
G9: JP5.16, U1.45 (OUTG9)
G10: JP5.7, U1.36 (OUTG10)
G11: JP5.1, U1.30 (OUTG11)
G12: JP5.19, U1.48 (OUTG12)
G13: JP5.13, U1.42 (OUTG13)
G14: JP5.10, U1.39 (OUTG14)
G15: JP5.4, U1.33 (OUTG15)
GND: C1.2, C2.-, JP1.1, JP4.26, JP5.26, U1.29 (GND_2), U1.56 (GND), U1.57 (THERMAL_PAD)
GSCLK: JP1.3, U1.55 (GSCLK)
R0: JP4.20, U1.8 (OUTR0)
R1: JP4.14, U1.14 (OUTR1)
R2: JP4.11, U1.17 (OUTR2)
R3: JP4.5, U1.23 (OUTR3)
R4: JP4.23, U1.5 (OUTR4)
R5: JP4.17, U1.11 (OUTR5)
R6: JP4.8, U1.20 (OUTR6)
R7: JP4.2, U1.26 (OUTR7)
R8: JP5.23, U1.52 (OUTR8)
R9: JP5.17, U1.46 (OUTR9)
R10: JP5.8, U1.37 (OUTR10)
R11: JP5.2, U1.31 (OUTR11)
R12: JP5.20, U1.49 (OUTR12)
R13: JP5.14, U1.43 (OUTR13)
R14: JP5.11, U1.40 (OUTR14)
R15: JP5.5, U1.34 (OUTR15)
SCLK: JP1.5, U1.2 (SCLK)
SIN: JP1.4, U1.1 (SIN)
SOUT: SOUT.1, U1.28 (SOUT)
VCC: C1.1, C2.+, JP1.2, JP4.25, JP5.25, U1.54 (VCC)

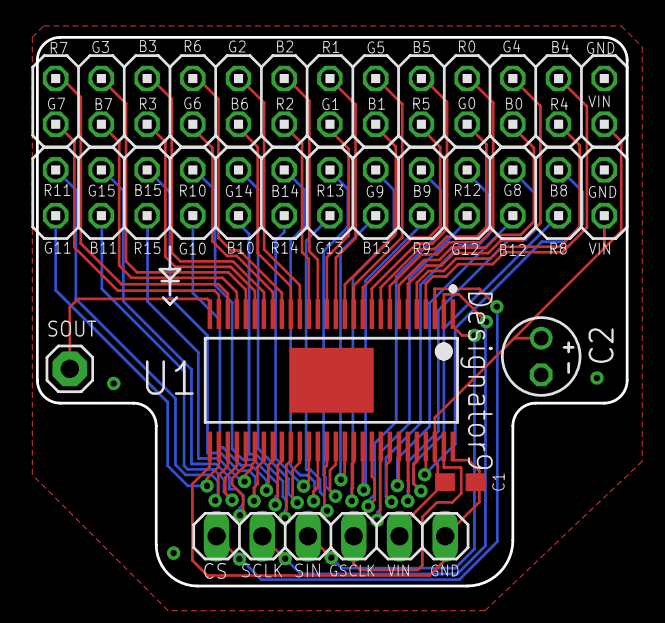
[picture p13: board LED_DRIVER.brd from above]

Board: 2 copper layers, 32.8 x 30.5 mm, 7 parts (0 on the bottom side), 55 nets.

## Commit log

2020-10-20 init repo
    [28ChFNIRS.brd, 28ChFNIRS.sch]
2021-02-18 Finished draft, time to test!
    [28ChFNIRS.brd, 28ChFNIRS.sch, Stiffener_BOT.gbr, Stiffener_TOP.gbr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]
2021-02-18 added a few mounting holes
    [28ChFNIRS.brd]
2021-06-28 16 Channel version (forehead-sized dense array)
    [16ChFNIRS.brd, 16ChFNIRS.sch, 16ChFNIRS_centroid.csv, Stiffener_BOT.gbr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]
2021-06-29 edit jumpers
    [16ChFNIRS.brd, 16ChFNIRS.sch, Stiffener_BOT.gbr, Stiffener_TOP.gbr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]
2021-06-29 more stiffener
    [16ChFNIRS.brd, 16ChFNIRS.sch, Stiffener_BOT.gbr, Stiffener_TOP.gbr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]
2021-07-24 add LED driver, shuffle repo
    [16ChFNIRS.brd, 16ChFNIRS.sch, 28ChFNIRS.brd, 28ChFNIRS.sch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]
2023-03-26 new revisions
    [16ChFNIRS.brd, 16ChFNIRS.sch]
2023-03-28 cam files
    [Profile_NP.gbr, Profile_P.gbr, copper_bottom.gbr, copper_top.gbr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]
2023-03-28 other gerbs
    [Profile_NP.gbr, Profile_P.gbr, copper_bottom.gbr, copper_top.gbr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]
2023-04-14 fixed connector stiffener
    [16ChFNIRS.brd]
2023-04-15 added wip sensor simulation
2023-05-05 add a recording test
    [Stiffener_BOT.gbr, Stiffener_Top.gbr, drill_1_16.xln, gerber_job.gbrjob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]

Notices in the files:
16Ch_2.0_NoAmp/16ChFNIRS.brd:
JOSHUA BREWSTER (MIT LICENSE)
